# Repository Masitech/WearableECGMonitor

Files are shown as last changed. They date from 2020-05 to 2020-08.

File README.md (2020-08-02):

# WearableECGMonitor

ECG Monitor

result

result2

Project Report (110 pages) : https://www.mahmed.tech/wp-content/uploads/2020/05/Project_Report_MAhmed-converted-compressed.pdf 

## 1.1 Background

The IoT (internet of things) field in wearable healthcare has received a lot of attention in the last
few years due to advancement in computing paradigms: cloud computing, fog computing and
edge computing. Machine learning on the cloud has revolutionized traditional healthcare.
ECG monitors is not a new concept, it has been around the medical environment for many
decades. In the last few years, technology has started appearing in many wearable devices such
as smartwatches (apple watch 4+) and dedicated standalone products such as AliveCor's
KardiaMobile[3]. Most of the designs use 3 wires: 2 wires for bipotential input and the third wire
for body bias (common-mode rejection).

## 1.2 Aim

This project aims to design a low power battery operated wearable device with wireless
capability that can measure ECG from the bipotential single channel. The system should be
lightweight and small since it will be worn for a long period without a battery recharge.
Use professional tools & software platforms to design the system which is relevant in the
embedded systems industry.
Understand low level embedded systems and overcome problems which are specific to the
project using OEM datasheet/documentation. 

## 1.3 Objective

* Small custom-designed embedded arm cortex board using small SMD parts (0603 or
smaller).

* Develop low power wearable hardware that can be powered from a small battery.

* Develop onboard battery management system for charging lipo battery.

* Implement low power wireless capability using BLE.

* Design and implement embedded firmware using RTOS

* Use of UART, SPI, PWM, SAADC, Timers and interrupts in the firmware using
low-level hardware coding and API.

* Use of commercial development software and tools.

## 1.4 Technical Requirement / Tools

During the development phase of this project, the following tools were used, and it would be
essential to have access to these tools for future continuation of the work.

Software IDE: Keil uVision 5 

JLink Debugger / STLink Programmer: Used to flash the microcontroller.

J-Flash Light v6.54 (Tool to flash hex file)

nRF Bluetooth Connect App for Bluetooth Debugging (Android)

FTDI (USB to Serial) Module - UART communication

Eagle Autodesk to modify the schematic

Embedded C++/C, JavaScript, Bluetooth GATT, Max30003 AFE, Mbed OS, nrfSDK15

Optional: Tools that can be helpful.

SamacSys PCB Library: Excellent tool to get component footprint and save time

Notepad++ : Generic text editor, highly recommended

UART serial monitor: Arduino Serial Monitor, Termite

Plotting ECG Waveform: Arduino Plotter, Windisp (Custom Tool)

Multimeter, Oscilloscope & SMD soldering skills 

## 2. System Design 

Systemm Design

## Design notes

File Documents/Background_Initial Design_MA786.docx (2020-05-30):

Wearable ECG Monitor

University of kent

Masum Ahmed Ma786

2019

# 1.0.0 Introduction

The IoT (internet of things) field in wearable healthcare has received a lot of attention in the last few years due to advancement in computing paradigms; cloud computing, fog computing and edge computing. Machine learning on the cloud has revolutionized traditional healthcare which has led to the surge of new smart health devices. There is a non-invasive glucose monitor which can track glucose levels throughout the day. Omron is developing a smartwatch which can take blood pressure measurement using traditional methodology but at a much smaller scale. Google is using deep learning for detection of eye disease in diabetic patients with outstanding results [1].

Due to increasing world population especially the ageing population, there has been a massive strain on the healthcare system worldwide affecting millions of people. Traditional doctor-patient interaction has lost its effectiveness. The healthcare system as we know is changing from reactive treatment of illness at the hospital to preventive and personalized intervention. Artificial intelligence is getting increasingly sophisticated at emulating humans do so but more efficiently, quicker and cheaper. The potential for AI in the healthcare ecosystem is vast. Smart healthcare devices collect large amounts of processable data which can be examined in real-time and stored on a database to be viewed later. Interactions between doctor and patient are more efficient and patient-orientated since doctors can make better decisions.

The project aims to develop a small battery-powered ECG device that can be worn on the body.

While smart wearable ECG device is not as accurate as a full-scale 12 lead electrocardiograph, it has other significant advantages: it can be worn all day every day. It can collect data throughout the day across a wide range of activities. The more data it collects better preventive model can be established that is personalized to the patient. A large amount of data can also be used to establish patterns using machine learning and predict potential health problems before they arise.

## 1.1.0 Aim and Objectives

- Design a low power wireless ECG acquisition which can operate continuously for a day without recharging.
- Design an Algorithm to evaluate ECG and extract breathing rate, heart rate and heart rate variability.
- Use standard communication protocols such as BLT5 / Thread to connect to a gateway device (smartphone, raspberry pi etc.)
- Design an android based app to display the data in real-time.
- Setup cloud service for medical professionals to access the data remotely.

Deliverables:

- A low power microcontroller system with a biopotential sensor for ECG measurement. (Hardware)
- Custom buck-boost power circuitry with high efficiency and low idle current consumption.
- Voltage reference circuit to provide clean power reference for analogue measurements.
- Embedded firmware that can detect heart rate from ECG data & wireless communication using the Bluetooth 5.1 protocol on-chip.
- Implement features such as deep sleep, variable transmission power to save battery.
- An android app using java environment to display data in real-time.
- Web app using JavaScript to display historical data for health profession analysis.

# 2.0.0 Background Research

## 2.1.0 Theoretical Foundation: ECG Waveform

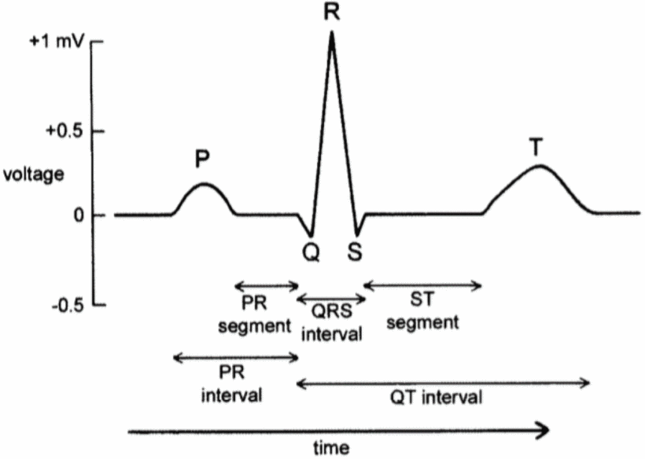
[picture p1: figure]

Figure 1 ECG waveform for one cardiac cycle

ECG measures the bio-potential generated by different contraction of the ventricles. The electrical impulse is generated in the sinoatrial node located in the atria [9]. The p wave as shown in figure 1 indicates atrial depolarization (atrial systole). There is a slight delay from the end of the P wave and the start of the QRS complex. This is caused by a cluster of cells called the atrioventricular node. This delay allows the atria to contract before the ventricle contracts. The QRS complex indicates ventricular contraction and depolarization (ventricular systole), this is caused by the electrical impulse moving from the AV node (atrioventricular node) through the bundle of His where it splits into the right-left bundle and then to the Purkinje fibres as shown in figure 2.

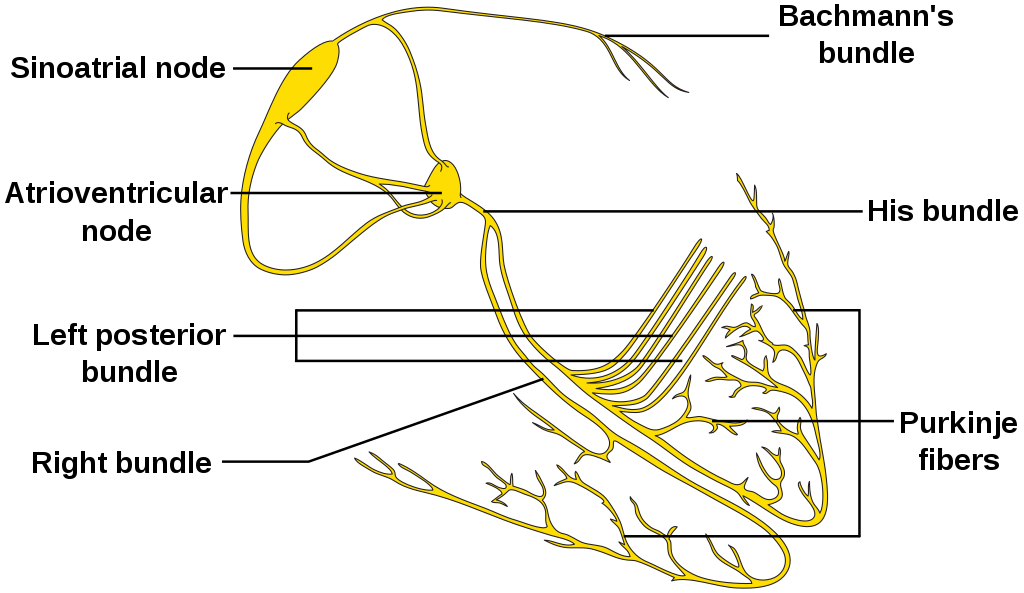
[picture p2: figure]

Figure 2 Electrical path of the heart during the cardiac cycle

In this project, I am only interested in the QRS complex, specifically the peak R amplitude from which the heart rate and heart rate variability will be calculated.

## 2.2.0 Technological State

Wireless technology and smart biosensors AFE (analogue front end) are the backbones of the smart healthcare system. There is a wide range of different wireless technology today supported by consumer devices: Wi-Fi, Bluetooth / BL Mesh, Thread, ANT, RFID, Zigbee, GSM/3G/4G. There are pros and cons to using all of these and specific technology is suited to certain project and environment.

There are two commonly used techniques in the industry to measure the heart rate, PPG (Photoplethysmography) and EEC (electrocardiography). PPG uses low-intensity infrared light to sense the change in blood flow during the cardiac cycle. The voltage signal from the receiver is inversely proportional to the volume of blood flowing. PPG is less accurate, more susceptible to motion artefact and consumes more power. The waveform of the PPG sensor contains fewer data related to the cardiac cycle [11][12].

## 2.3.0 Hardware Design and Implementation

There are multiple different approaches to designing analogue and digital hardware for ECG acquisition. One of the most advanced methods has been presented by Dr Shihui Yin et al from the University of Arizona who designed and fabricated the analogue hardware on 65nm CMOS logic [13]. It is extremely low power only 1.06µW during operation. Unfortunately, this is outside the scope of this project due to budget, time, tools limitation. It will be much easier to work with consumer IC’s and design custom PCB to integrate all the AFE’s and processing hardware. This approach was taken by theses research projects [8][14][15].

### 2.3.1 Microcontroller

ATmega328P (Arduino) 8bit microcontroller was used to acquire the ECG voltage data in [14][8] and MSP430 in [15]. The microcontrollers were chosen by the researchers because it has a lot of third-party libraries and interfacing them with a third-party device is well documented. However, the microcontrollers are slow only 16MHz, uses old 8 & 16-bit architecture, consumes a lot of power, the ADC resolution is limited to 8bits (atmega328P) and 10 bits on the MSP430 and most importantly Bluetooth is not integrated.

### 2.3.2 ECG Electrodes

Ag/AgC1 electrodes are widely used in ECG measurement due to their low skin to electrode contact impedance however, they are not suitable for continuous long-term measurement as it can irritate the skin and cause skin allergies [17]. An alternative dry electrode made from metal, conductive rubber or conductive fabric was found to be suitable for long term use [18][19].

### 2.3.3 Source of Noise

List of significant sources of noise in ECG data [22]

- Mains power lines produce 50Hz periodic interference.
- Movement can cause loss of contact between the skin and the electrode; this can result in a fast change in the potential difference in the signal which will result in false-positive readings.
- Muscle movement can cause noise from the electrical activity of the muscle.
- Respiration and general movement can cause baseline wander.

Signal to noise ratio can be improved by eliminating the above sources of noise. This can be done by implementing high and low pass filter and some software filtering.[8]

### 2.3.4 Acquiring ECG Data

“ECG input signal on the skin is very low in amplitude (<1 mV) and noisy. ECG voltage signal must be amplified, then high pass filtered to get rid of DC skin potential and battery effects. Then it must be low pass filtered to cut off high-frequency noise and mains interference” [16]. There seem to be many ways to achieve this. Traditionally electrodes would be connected to a series of operational amplifiers configured to perform the above function (amplify, high pass, low pass). However, this method is bulky because it requires a lot of components and consumes a significant amount of power.

The custom-designed integrated circuits prosed, in the study [14]. The researcher used the AD8232 IC which is a single chip with integrated OpAmps. The resistors connect to the pins of the AD8232 pins which can be altered to configure and set limits for the filters. Using the above configuration reduces PCB space however the design is still limited by the resolution of the ADC on the microcontroller.

### 2.3.5 EMI – Human Antenna Effect

The user body can act as an antenna which can pick up electromagnetic signals mostly in the range of 50 – 60 Hz common mode noise from mains electrical AC power lines. A large amount of electromagnetic interference is coupled to the user’s body through the skin [20]. The source of noise must be eliminated in hardware. The solution provided by the researcher uses the right leg as common noise input which can be rejected from the original differential ECG signal, more on this on selection 2.2.6 and why it is not viable according to [21].

### 2.3.6 Common Mode Rejection Ratio (CMRR)

Having a ground electrode to reduce noise is not suitable in a wearable device because it will introduce high leakage current during operation [21]. A system with high CMRR can be achieved by implementing an extra stage in the hardware signal processing. As mentioned in 2.2.5 the body is good at picking up common mode signals; noise that affects both electrodes equally. Achieving a system with a high common-mode ratio is important [22].

### 2.3.7 Data Storage

Continuous measurement of ECG will result in a lot of data. To avoid loss of data when the device is not connected to a suitable Bluetooth device or if the signal connection is lost data must be stored in a suitable place.

MicroSD card integration is simple and used by many research projects [8][15]. If the raw ECG data is not kept rather the induced HR, then it will be suitable to use the onboard flash in the microcontroller itself. Micro SD card may not be suitable in a low power wearable device. It can consume around 100mA at 3.3V. An alternative option would be to use NOR flash chips.

### 2.3.8 Sampling Frequency

It was determined sampling frequency low as 50Hz can be used to obtain HRV by software interpolation [23]. The researcher tested a range of sampling frequency from 5KHz to 50Hz and run statistical tests on each of the acquired data. The researcher also noted the R peaks were slightly distorted due to low sampling frequency. The optimal range of sampling rate for spectral analysis of HRV parameters is between 250 and 500 Hz [24].

## 2.4.0 Market Research

### 2.4.1 Commercial Products

Amazfit Health Band 1S Is a PPA based smart band with an ECG sensor. It uses PPA technology to continuously monitor the heart rate if it detects arrhythmia then it alerts the user and asks them to take an ECG reading by placing a finger on top of the band. The data is sent to the cloud which is then processed by AI. The data can be accessed by the user (free for the first 6 months). The device is manufactured and developed by a Chinese company and is not widely adopted in the west.

Welch Allyn TAGecg sensor Is an ECG based chest sensor which continuously records the ECG of the user. It examines the heart rate and has built an algorithm in the local system to detect arrhythmia. The data is also synced to the cloud where it can be further examined by the medical profession. The device is manufactured and developed by Welch Allyn an American company who develops a medical device for private healthcare in America.

# 3.0.0 System Design

The system will have bipotential ECG AFE sensor which will take differential measurement from 3 wire electrode (ECG P, ECG N). It will be powered from the +3.3V and +1.8V rail. The ECG sensor will be interfaced to the microcontroller via SPI (Serial Peripheral Interface).

To reduce PCB space and power consumption a microcontroller with wireless capability will be utilised. It will be interfaced with NOR flash to store data while the system is not connected to an external Bluetooth master node. It will be time synced relative to the connected master node since it does not have a real-time clock. Alongside the ECG data, relative timing information will be stored. This information is important to calculate the heart rate & heart rate variability of the user.

The embedded hardware will connect to a smartphone via Bluetooth and send its stored data. This data will be temporarily stored on the phone then uploaded to a server connected to the internet. There will be a companion app on a smartphone which will display current data send by the embedded hardware and historic data stored on an online database. For third party public access there will be a web portal where historic data can be viewed.

The system will have the ability to show live ECG and temperature data in real-time through the android application. At this stage, the mobile phone will not be doing any preprocessing just acting as a monitor for the data.

The cloud system will be set up on a separate computer connected to the internet. It will use MySQL database to store the data which can be accessed on via time and key events. The system will only focus on the single-user system to reduce design complexity.

Website hosted on a server will be utilized to develop a web portal to access data from the database for public usage. The system will be protected from unauthorised access by user login.

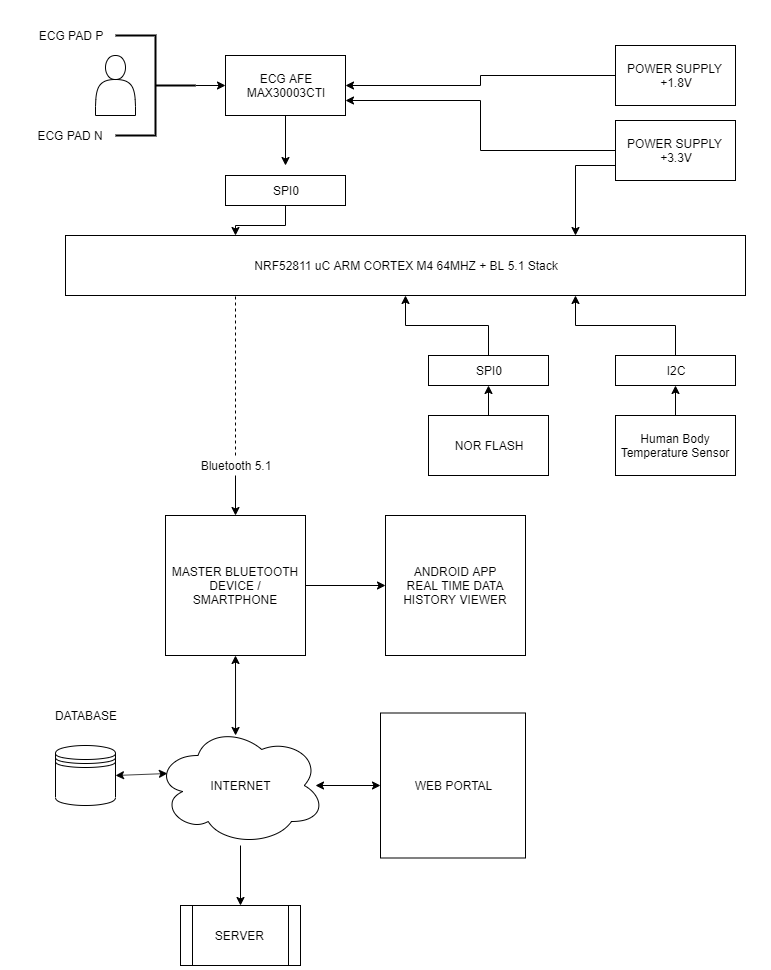
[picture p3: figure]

Figure 3 High-level system architecture diagram

## 3.1.0 Microcontroller

Espressif ESP32 WIFI & BLE is an alternative option since I have used this soc before, however, this would not fit the project since the power consumption during transmission is too high 100mA vs ~4.6mA (nRF52811). The footprint of the IC is too small to solder by hand and the processor is over specced for what I need it for. 240mhz @ dual-core is too much power. It also implements an older protocol: Bluetooth 4.2.

Nordic Semiconductor nRF52811 is a low power 64mhz arm cortex M4 based microcontroller with Bluetooth 5.1 protocol, including Long Range and Direction Finding, 802.15.4, Thread and Zigbee in a 6mm² 48pin QFN package. The microcontroller has low power consumption during idle and only 4.6mA during transmission at 0dB this makes it ideal for wearable devices.

When designing with this microcontroller the SPI1 instance cannot be used while using I2C peripheral because they both share the base memory address.

I have chosen this microcontroller over Arduino(atmega328P) and mbed (lpc1768) because it has the Bluetooth stack integrated into the microcontroller. The datasheet is comprehensive and there is a lot of online support. In industry, semiconductor devices are widely used where esp32 and Arduino are limited to maker and research projects due to licencing incompatibility.

## 3.2.0 Integrated Biopotential Sensor

BMD101 Is a popular IC used in commercial ECG band due to its size and performance, however, availability is non-existent in the EU/UK/US market. The datasheet is only 14 pages and covers the basic aspects of the IC.

MAX30003CTI+ Ultra-Low Power, Single-Channel Integrated Biopotential dual electrode. It’s a complete analogue front-end solution for wearable applications. It packs all the operational amplifiers internally in a small QFN package. This is an improvement upon Dr B. Babusiak analogue design [8] because it saves PCB space, power-efficient and has higher CMRR.

The IC has built-in R-R detection which uses the Pan-Tompkins algorithm [2] to determine the heart rate. However raw data can be sent to the microcontroller by changing the registers. It simplifies filtering by internally incorporating a low and high pass filter reducing the external components. The device can also be configured to output raw 15.5bit ADC reading (sample and hold) without any modification.

Baseline wander is an issue with ECG (low-frequency noise) which can be expensive (compute time) in software to fix. The AFE tries to take care of this at a hardware level. The gathered data has a high signal to noise ratio (SNR). There are three recommended options for the cut off frequency: 4.4Hz, 0.4Hz, and 0.04Hz. Setting the cut off frequency to 4.4Hz provides the most motion artefact rejection, the trade-off is waveform quality.

The device’s ECG channel contains an input amplifier that provides low-noise, fixed-gain amplification of the differential signal (ECG Positive, ECG Negative), rejects differential DC voltage due to electrode polarization, rejects common-mode interference primarily due to AC mains interference, and provides high input impedance to guarantee high CMRR (Common Mode Rejection Ratio).

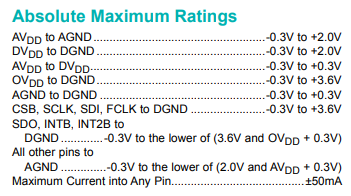
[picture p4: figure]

Figure 4 Pin input voltage rating from max30003 datasheet

The datasheet (figure 4) shows AVDD -> AGND must be <+2.0V and DVDD -> DGND <+2.0V this means I need dual voltage rails 3.3V and 1.8V since the AFE is not high power I will use low IQ (quiescent current) low dropout linear regulator (LDO). There are 2 different grounds, AGND & DGND. The ground will be connected to each other by a 0 ohms resistor.

##### 3.2.1 Lead Bias

The ECG AFE limits the input of ECGP and ECGN DC input common-mode range to VMID ±150mV. This means if there’s a significant bias voltage it can result in the signal getting clipped at VMAX and VMIN resulting in data loss. This can be fixed using external lead biasing resistor, fortunately, this IC has internal selectable lead biasing resistor: 50MΩ, 100MΩ and 200MΩ CNFG_GEN (0x10) register can be used to select a configuration.

##### 3.2.2 Interfacing ECG AFE with an MCU

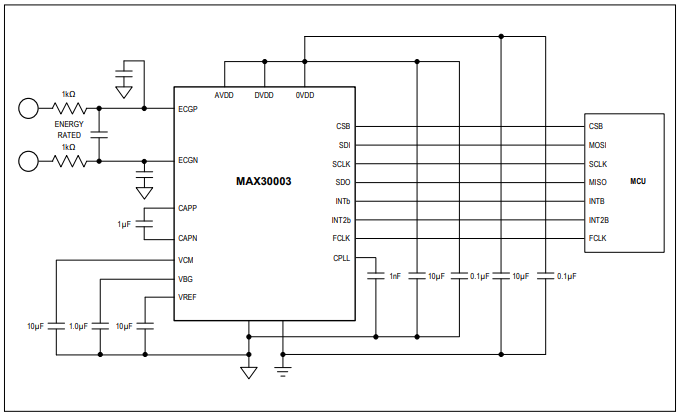
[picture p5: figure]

Figure 5 ECG AFE interfacing with a generic micro-controller

Integration to nrf52811 microcontroller GPIO pin can be configured as required in software, therefore, it does not matter which pin the corresponding pins connect to. MOSI, SCLK, MISO are SPI specific pins while INTb and INTa are interrupted pins to indicate when data is ready. FCLK is the clock to max30003 this will be a GPIO pin controlled under interrupt to change the clock edge. CSB is chip select to reliable / disable SPI communication there can be multiple devices on the SPI interface.

Name | Function
CBS | Active low chip select input. enables the serial interface
SDI | Serial Data Input. SDI is sampled into the device on the rising edge of SCLK when CSB is low
SCLK | Serial Clock Input. Clocks data in and out of the serial interface when CSB is low
SDO | Serial Data Output. SDO will change state on the falling edge of SCLK when CSB is low. SDO is high z when CSB is high.
INTb | Interrupt Output. INTB is an active low-status output. It can be used to interrupt an external device.
INT2b | Interrupt 2 Output. INT2B is an active-low status output. It can be used to interrupt an external device.
FCLK | External 32.768kHz Clock that Controls the Sampling of the Internal Sigma-Delta Converters and Decimator.

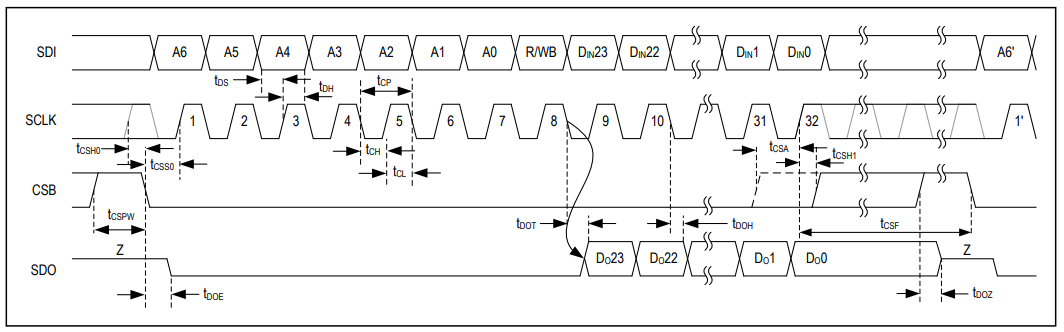
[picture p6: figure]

The timing characteristics (figure 6) is used to write the SPI driver software. It outlines timing limits and pins logic during operation, it also outlines when the data is ready to be read and when to write. The full table can be accessed on page 7 of the datasheet.

Figure 6 Timing characteristics max30003 datasheet p7

## 3.3.0 Power Supply

For the project, it makes sense to use a rechargeable battery. Lithium-ion polymer battery (LIPO) comes in small packages with a large capacity. Making it suitable for wearable / portable device since it can store a lot of power in a small size. The short circuit current for LIPO battery is a lot higher than alkaline batteries, therefore, can cause fires easily if not monitored strictly [7]. The proposed design to monitor the battery voltage while charging. This is a backup protocol in case the charging IC is misbehaving see figure 7 for power supply design diagram.

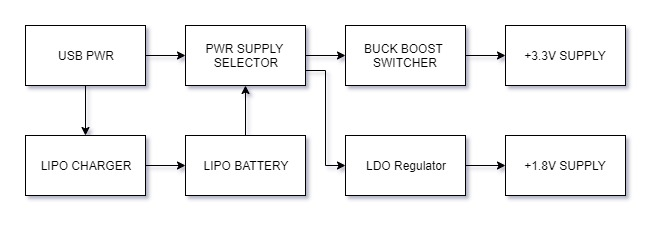
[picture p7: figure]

Figure 7 Power supply system design

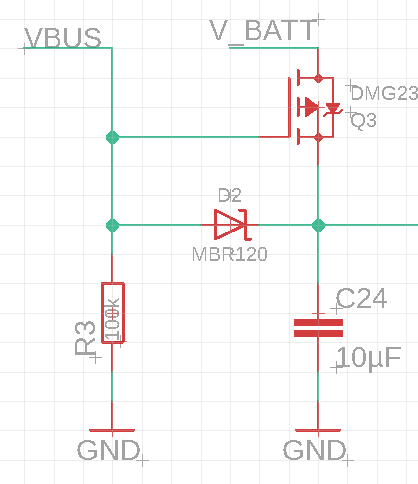
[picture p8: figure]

The normal battery level is 3.7V and it can range from 4.2V to 2.2V. Since the system voltage level ist at 3.3V, the power supply must be in buck configuration above 3.3V and in boost configuration below 3.3V. When the USB charging cable is connected, the system will be powered from USB power rather than battery power. This resolves the issues of charging the battery while providing power. This is implemented using N channel MOSFET (Q3) and a diode. When the USB cable is connected Q3 is disabled since gate voltage is at VBUS, this cuts off the V_BATT power in. When the USB cable is disconnected the gate voltage is GND (pulled down by R3 resistor) which enables Q3. D2 diode stops the current flowing in the opposite direction note figure 8 for further details.

Figure 8 Digital logic to select USB power over LIPO power if it is present.

### 3.3.1 Battery Charger

To charge the LIPO battery MCP73831 IC will be used from microchip because it requires minimal external components and it is in a footprint that can be soldered by hand without too much effort. This is different from the one used in [8], MCP7337 was not chosen because it consumes a lot more PCB space. mcp73837 has a feature that is not available on the mcp73837 due to limited pins. To get the same level of capability as the bigger brother I will not be following the recommended application implementation design since I want to control the charger IC using the microcontroller. Unfortunately, this IC does not have an enable disable pin to control the IC unlike mcp73837 and the status pin is configured to connect to an LED. I want the microcontroller to know when the battery is charged and when it is charging. Figure 9A shows a typical application design and figure 9B shows the modified design.

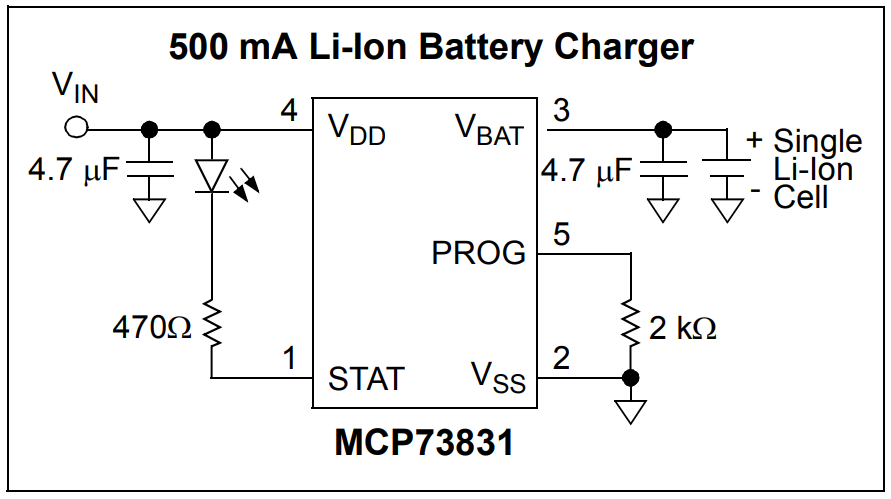
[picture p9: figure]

Figure 9A Typical design implementation of MCP73831

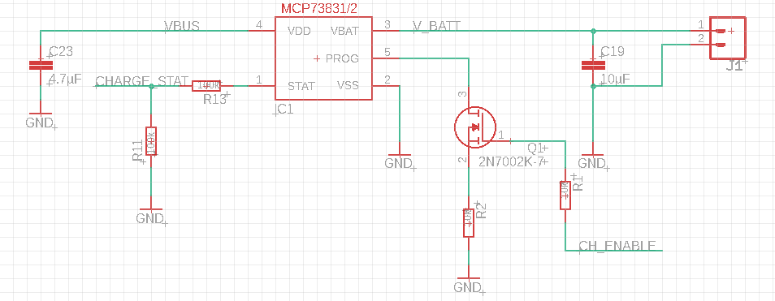
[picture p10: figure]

Figure 9B Custom design implementation proposal

I have used a P channel MOSFET with the gate connected to a GPIO pin on the microcontroller. The source to base resistance is around 1 ohm so it should have minimal effect on the charging current which determined by the formula (1) (1 ) Ireg= (1000v)/(Rprog) A charge current programming resistor must be connected from PROG to VSS. If the PROG pin is open or floating, the MCP73831/2 is disabled and the battery reverse discharge current is less than 2 µA extract from mcp73831 datasheet. I am not using reverse battery protection diode because it will consume power while idle and the voltage drop is significant.

Where Ireg = in milliohms, Rprog = in kilo-ohms.

Charge status pin is tri-state and requires a pull-down or a pull-up. During the logic high, the status pin VDD is same as STAT which can be as high as 5V, therefore, I have used a resistor divider.

## 3.4.0 Software Architecture

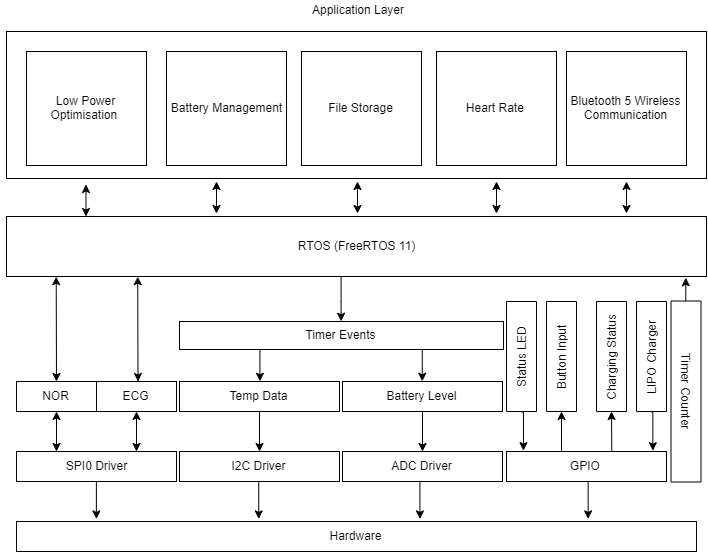
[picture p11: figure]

Figure 10: Software design layers

The embedded software will consist of subprograms which will be responsible for different tasks. Figure 10 outlines the smaller components of the software breaking it down into layers bottom being closer to the hardware. The higher layers are general-purpose code, they are generally less restricted by the hardware making it more portable.

FreeRTOS will be used as the real-time operating system because it is free and open-source. On top of the RTOS will be my custom application code among the Bluetooth stack from a Nordic semi (manufacture). Below the RTOS will be the hardware determined code, responsible for controlling the peripherals on the microcontroller.

## 3.5.0 Android App

Andriod studio IDE and java programming language will be used to create the android application. The resources such as images and gfx design will be obtained from openGFX package. It will be my first time developing an android application; therefore, extra time was given on the grant chart to learn java and JavaScript. Java was chosen over Kotlin because it has more resources and my course teaches java. JavaScript will be used to design buttons, logos, animation etc. I hope to interface the app with Bluetooth hardware on the android phone and connect to the embedded hardware.

## 3.6.0 Bluetooth 5 Communication

Bluetooth is a standardised protocol for transmitting and receiving data wirelessly on the 2.4GHz channel. Its secure, short-range, low power and cost and requires minimal external hardware. Bluetooth has standardised test of rules and specification which differentiates it from other standards: WIFI, ZigBee, ANT and Thread.

The BL is standard is published and maintained by the bluetooth.com organisation. The specification outlines all aspects of Bluetooth however its 2985 pages long.

Bluetooth network utilises master/slave model to control when the device can transmit data. Every Bluetooth device has a unique 48-bit MAC address (BD_ADDR) presented in 12-digit hexadecimal format. Most significant half of the address identifies the manufacturer and the lower 24bit is the uniqueness. MAC address is used in software to identify hardware and keep track of communication between that hardware and itself. The microcontroller I will be using has Bluetooth integrated. I will be using the Bluetooth stack provided by the manufacturer (Nordic Semiconductor).

# 4.0.0 Development Tools

## 4.1.0 Keil 5 MDK

Keil will be used as programming and flashing platform because it provides good compatibility with the chosen microcontroller and I have used this IDE during my year in industry. I will be using the NRF SDK on this platform. Among their own software library integrated into the IDE itself. Keil allows programming using debuggers such as Segger JLINK however the cost of a debugger is several times the budget of this project.

## 4.2.0 Windisp UART Communication

Windisp is a serial communication terminal, I will be using this tool extensively during development. It will communicate with the embedded system using UART and display data in a readable format. Unfortunately, it’s not able to do graphs directly but it is able to create.CVS files; using excel I will be able to create trend files and graphs.

## 4.3.0 Programming Custom Board

The microcontroller cannot be programmed via UART (RS232). Which is a major limitation because it means I must use SWDIO pin to program the device. This requires external tools which are very expensive. The NRF52DK has a secondary processor used just for programming and interfacing it to MBED. I will be utilising the dev kits secondary processor to flash my microcontroller.

# 5.0.0 Risk Analysis

Risk | Precaution Taken to Minimise Risk
Out of stock parts | All the parts used in the project can be sourced from multiple different companies as well as the manufacturer.
Incompatible software | I have downloaded and installed all the software already to make sure its compatible with my system
Delay in a custom board | I will be using development boards while the custom board manufactured and assembled.
Damaged PCB | I have given myself time to manufacture 2 versions of the PCB.
Design / Logic Fault | Before starting the layout, the schematic will be checked to make sure everything is connected correctly.
Running out of time | I am planning to implement an incremental development process. Core things like hardware and ECG data will be a priority then will come the extra features.
Hard stuck coding | I will use a tool called windisp to debug the code to find where the problem is. Also, debuggers tools such as Segger JLink integrated on the dev board can be used to resolve coding issues.
Damaging boards while soldering | I will order multiple copies of the same version of the PCB if one gets damaged it will not affect the progression of the project.

# 6.0.0 Project Plan and Budget

## 6.1.0 Bill of Material

Quantity | Parts ID | Price (1 unit) | Supplier | Stock Code
2 | NRF52811 | £3.19 | Mouser | 949-NRF52811-CAAA-R
2 | MAX30003 | £7.33 | Mouser | 700-MAX30003CTI+
1 | AT25QF128A-SHB-T | £1.25 | Mouser | 988-AT25QF128A-SHB-T
1 | MAX30205 | £1.92 | Mouser | 700-MAX30205MTA+
| SMD Resistors | £8.00
| SMD Cap | £8.00
| SMD Inductor | £5.00
2 | MCP73831 | £0.47 | Mouser | 579-MCP73831T-2ACIOT
1 | Turnigy 200mAh | £1.89 | Hobby King | 9067000498-0
2 | LDO | £0.25 | Mouser | 579-MCP1811AT-042/TT
1 | Max30003 DK | £19 | Mouser | 700-MAX30003WING
5 | PCB | £4
1 | JLINK Programmer | - | -
1 | Nrf5240 UBB Dev Board | £8.52 | Mouser | 949-NRF52840-DONGLE
| Total | £94.81 | -

## 6.2.0 Gantt Chart

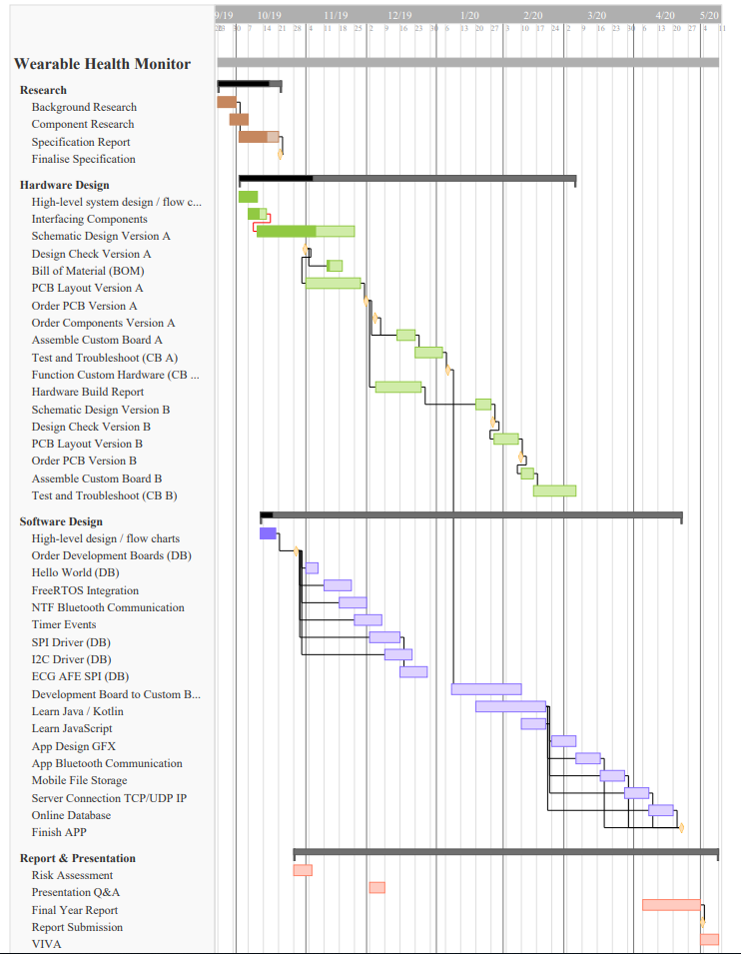
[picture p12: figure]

# 7.0.0 References

[1]

Gulshan V, Peng L, Coram M, et al. Development and Validation of a Deep Learning Algorithm for Detection of Diabetic Retinopathy in Retinal Fundus Photographs. JAMA. 2016;316(22):2402–2410. doi:10.1001/jama.2016.17216

[2]

Pan, J. and Tompkins, W. (1985). A Real-Time QRS Detection Algorithm. IEEE Transactions on Biomedical Engineering, BME-32(3), pp.230-236.

[3]

P., Chiang, P., Tarng, D. and Yang, C. (2018). Mathematical derivation, circuits design and clinical experiments of measuring blood flow volume (BFV) at arteriovenous fistula (AVF) of hemodialysis (HD) patients using a newly developed photoplethysmography (PPG) sensor. 2018 19th International Symposium on Quality Electronic Design (ISQED).

[4]

Arun, U., Natarajan, S. and Rajanna, R. (2018). A Novel IoT Cloud-based Real-Time Cardiac Monitoring Approach using NI myRIO-1900 for Telemedicine Applications. 2018 3rd International Conference on Circuits, Control, Communication and Computing (I4C).

[5]

Rahman, A., Rahman, T., Ghani, N., Hossain, S. and Uddin, J. (2019). IoT Based Patient Monitoring System Using ECG Sensor. 2019 International Conference on Robotics, Electrical and Signal Processing Techniques (ICREST).

[6]

Nurdin, M., Hadiyoso, S. and Rizal, A. (2016). A low-cost Internet of Things (IoT) system for multi-patient ECG's monitoring. 2016 International Conference on Control, Electronics, Renewable Energy and Communications (ICCEREC).

[7]

Vitols, K. (2015). Lithium ion battery parameter evaluation for battery management system. 2015 56th International Scientific Conference on Power and Electrical Engineering of Riga Technical University (RTUCON).

[8]

Babusiak, B., Gala, M. and Borik, S. (2014). Hardware design of ECG data logger. 2014 ELEKTRO.

[9]

Anthony Dupre MS, MS Sarah Vincent, Paul A. Iaizzo, "Basic ECG Theory Recordings and Interpretation", Chapter Handbook of Cardiac Anatomy Physiology and Devices,

[10]

Chavdar Levkov, Georgy Mihov et al, "Removal of power-line interference from the ECG: a review of the subtraction procedure", Biomedical Engineering Online, 2005.

[11]

Lu, G., Yang, F., Taylor, J. and Stein, J. (2009). A comparison of photoplethysmography and ECG recording to analyse heart rate variability in healthy subjects. Journal of Medical Engineering & Technology, 33(8), pp.634-641.

[12]

Lu, G. and Yang, F. (2009). Limitations of Oximetry to Measure Heart Rate Variability Measures. Cardiovascular Engineering, 9(3), pp.119-125.

[13]

Yin, S., Kim, M., Kadetotad, D., Liu, Y., Bae, C., Kim, S., Cao, Y. and Seo, J. (2017). A 1.06 μw smart ecg processor in 65 nm cmos for real-time biometric authentication and personal cardiac monitoring. 2017 Symposium on VLSI Circuits.

[14]

Tanweer, M. and Halonen, K. (2019). Development of wearable hardware platform to measure the ECG and EMG with IMU to detect motion artifacts. 2019 IEEE 22nd International Symposium on Design and Diagnostics of Electronic Circuits & Systems (DDECS).

[15]

Chen, W., Chen, Y., Chou, C. and Fang, W. (2015). An EEG analog front-end design with wireless communication module for a portable EEG monitoring system. 2015 IEEE 5th International Conference on Consumer Electronics - Berlin (ICCE-Berlin).

[16]

Lacirignola, F. and Pasero, E. (2017). Hardware design of a wearable ECG-sensor: Strategies implementation for improving CMRR and reducing noise. 2017 European Conference on Circuit Theory and Design (ECCTD).

[17]

Ju-Yeoul Baeka, Jin-Hee An, Jong-Min Choi, Kwang-Suk Park, Sang-Hoon Lee. "Flexible polymeric dry electrodes for the long-term monitoring of ECG," Sensors and Actuators A: Physical, vol. 143, 2008, pp. 423-429.

[18]

S. H. N. Chang, Y. Ryu, K. Seunghwan, "Conductive rubber electrode for wearable health monitoring," in Proceesing of the 2005 IEEE Engineering in Medicine and Biology 27th Annual Conference, Shanghai, China, 2005. pp. 3479-3481.

[19]

Carey R. Merritt, H. Troy Nagle, and Edward Grant, "Fabric-based active electrode design and fabrication for health monitoring clothing," IEEE Transactions on information technology in biomedicine. vol. 13, 2009, pp.274-280.

[20]

Acharya, V., 2011. Improving common-mode rejection using the right-leg drive amplifier. Texas Instruments, pp.1-11.

[21]

Lacirignola, F. and Pasero, E. (2017). Hardware design of a wearable ECG-sensor: Strategies implementation for improving CMRR and reducing noise. 2017 European Conference on Circuit Theory and Design (ECCTD).

[22]

A. S. Barhatte, R. Ghongade, and S. V. Tekale, “Noise analysis of ECG signal using fast ICA,” 2016 Conference on Advances in Signal Processing (CASP), 2016.

[23]

S. Mahdiani, V. Jeyhani, M. Peltokangas, and A. Vehkaoja, “Is 50 Hz high enough ECG sampling frequency for accurate HRV analysis?” 2015 37th Annual International Conference of the IEEE Engineering in Medicine and Biology Society (EMBC), 2015.

[24]

G. D. Pinna, R Maestri, A. Di, R. Colombo, G. Minuco, "The accuracy of power spectrum analysis of heart rate variability from annotated RR lists generated by Holter systems", Physiological Measurement, vol. 15, no. 2, pp. 163-179, May 1994.

Section I: Project details
Project title: | Wearable ECG Monitor
Planned start date: 23/09/2019 | | Planned end date: 28/04/2020
Funder: | University of Kent

Section II: Applicant details
Applicant name: | Masum Ahmed
Department: | EDA
Email: Masum Ahmed | | Telephone number: 07410124124
Contact address: | 17 channel close Folkestone ct196qn

Applicant signature | M.Ahmed | Date | 16/10/2019

Section III: Students only
Supervisor: S. Hoque
Undergraduate ☒ | Masters ☐ | | Doctorate ☐ | Other (please specify)

Supervisor name | | Date
Supervisor signature

School REAG rep signature | | Date

If any question in Section IV(A) are answered ‘yes’:

1. Contact Nicole Palmer (University Research Ethics & Governance Officer) for advice
2. Send a copy of ethical approval to the Faculties Support Office, once received

If any questions in Section IV(B) are answered ‘yes’:

1. Complete full application form
2. Send to the Faculties Support Office for review by the Research Ethics Advisory Group (REAG)

If all questions in Section IV(A) and IV(B) are answered as ‘no’, send the completed and signed form to the Faculties Support Office.

Declaration: Please note that it is your responsibility to follow, and to ensure that, all researchers involved with your project follow accepted ethical practice and appropriate professional ethical guidelines in the conduct of your study. You must take all reasonable steps to protect the dignity, rights, safety and well-being of participants. This includes providing participants with appropriate information sheets, ensuring informed consent and ensuring confidentiality in the storage and use of data.

Section IV: Research Checklist

Please answer all questions by ticking the appropriate box:

A) Research that may need to be reviewed by an NHS Research Ethics Committee, the Social Care Research Ethics Committee (SCREC) or other external ethics committee (if yes, please give brief details as an annex) | YES | NO
Will the study involve recruitment of patients through the NHS or the use of NHS patient data or samples? | ☐ | ☒
Will the study involve the collection of tissue samples (including blood, saliva, urine, etc.) from participants or the use of existing samples? | ☐ | ☒
Will the study involve participants, or their data, from adult social care, including home care, or residents from a residential or nursing care home? | ☐ | ☒
Will the study involve research participants identified because of their status as relatives or carers of past or present users of these services? | ☐ | ☒
Does the study involve participants aged 16 or over who are unable to give informed consent (e.g. people with learning disabilities or dementia)? | ☐ | ☒
Is the research a social care study funded by the Department of Health? | ☐ | ☒
Is the research a health-related study involving prisoners? | ☐ | ☒
Is the research a clinical investigation of a non-CE Marked medical device, or a medical device which has been modified or is being used outside its CE Mark intended purpose, conducted by or with the support of the manufacturer or another commercial company to provide data for CE marking purposes? (a CE mark signifies compliance with European safety standards) | ☐ | ☒
Is the research a clinical trial of an investigational medicinal product or a medical device? | ☐ | ☒

If the answer to any questions in Section IV(A) is ‘yes’, please contact the Research Ethics & Governance Officer for further advice and assistance.

B) Research that may need full review by the Sciences REAG | YES | NO
Does the research involve other vulnerable groups: eg, children; those with cognitive impairment? | ☐ | ☒
Is the research to be conducted in such a way that the relationship between participant and researcher is unequal (eg, a subject may feel under pressure to participate in order to avoid damaging a relationship with the researcher)? | ☐ | ☒
Does the project involve the collection of material that could be considered of a sensitive, personal, biographical, medical, psychological, social or physiological nature. | ☐ | ☒
Will the study require the cooperation of a gatekeeper for initial access to the groups or individuals to be recruited (eg, headmaster at a School; group leader of a self-help group)? | ☐ | ☒
Will it be necessary for participants to take part in the study without their knowledge and consent at the time? (eg, covert observation of people in non-public places?) | ☐ | ☒
Will the study involve discussion of sensitive topics (eg, sexual activity; drug use; criminal activity)? | ☐ | ☒
Are drugs, placebos or other substances (eg, food substances, vitamins) to be administered to the study participants or will the study involve invasive, intrusive or potentially harmful procedures of any kind? | ☐ | ☒
Is pain or more than mild discomfort likely to result from the study? | ☐ | ☒
Could the study induce psychological stress or anxiety or cause harm or negative consequences beyond the risks encountered in normal life? | ☐ | ☒
Will the study involve prolonged or repetitive testing? | ☐ | ☒
Will the research involve administrative or secure data that requires permission from the appropriate authorities before use? | ☐ | ☒
Is there a possibility that the safety of the researcher may be in question (eg, international research; locally employed research assistants)? | ☐ | ☒
Does the research involve participants carrying out any of the research activities themselves (i.e. acting as researchers as opposed to just being participants)? | ☐ | ☒
Will the research take place outside the UK? | ☐ | ☒
Will the outcome of the research allow respondents to be identified either directly or indirectly (eg, through aggregating separate data sources gathered from the internet)? | ☐ | ☒
Will research involve the sharing of data or confidential information beyond the initial consent given? | ☐ | ☒
Will financial inducements (other than reasonable expenses and compensation for time) be offered to participants? | ☐ | ☒
Are there any conflicts of interest with the proposed research/research findings? (eg, is the researcher working for the organisation under research or might the research or research findings cause a risk of harm to the participants(s) or the researcher(s) or the institution?) | ☐ | ☒

If the answer to any questions in Section IV(B) is ‘yes’, please complete the full application form and send to the Faculties Support Office

C) Security Sensitive Material | YES | NO
Does your research involve access to or use of material covered by the Terrorism Act? (The Terrorism Act (2006) outlaws the dissemination of records, statements and other documents that can be interpreted as promoting and endorsing terrorist acts. By answering ‘yes’ you are registering your legitimate use of this material with the Research Ethics Advisory Group. In the event of a police investigation, this registration will help you to demonstrate that your use of this material is legitimate and lawful). | ☐ | ☒

Wearable ECG Monitor Masum Ahmed

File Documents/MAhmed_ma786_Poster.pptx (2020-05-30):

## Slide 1

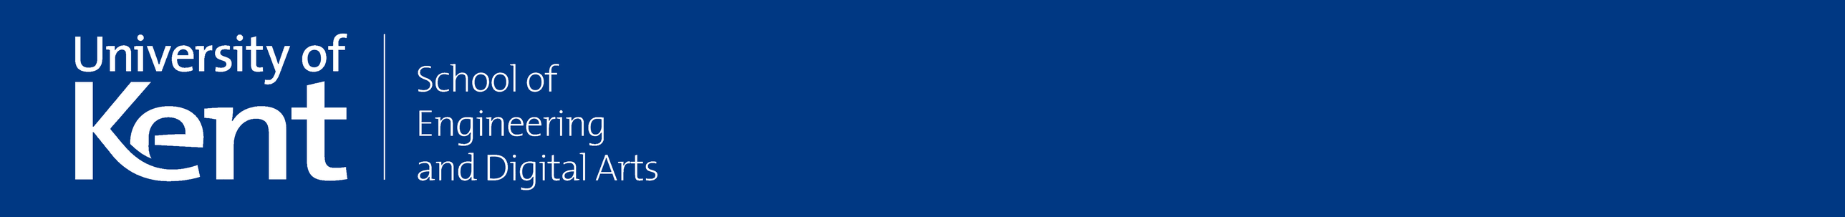
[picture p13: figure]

Wearable ECG Monitor

By M Ahmed Supervisor: Dr S Hoque

INTRODUCTION

The IoT (internet of things) field in wearable healthcare has received a lot of attention in the last few years due to advancement in computing paradigms: cloud computing, fog computing and edge computing.
This project aims to develop a highly integrated battery-powered wearable embedded system with wireless capability that can measures ECG from bipotential input. To get an understanding of engineering development that moves past the educational / preconfigured hardware module and into the industrial territory. Implementing custom design at chip-level using manufacture provided datasheets.

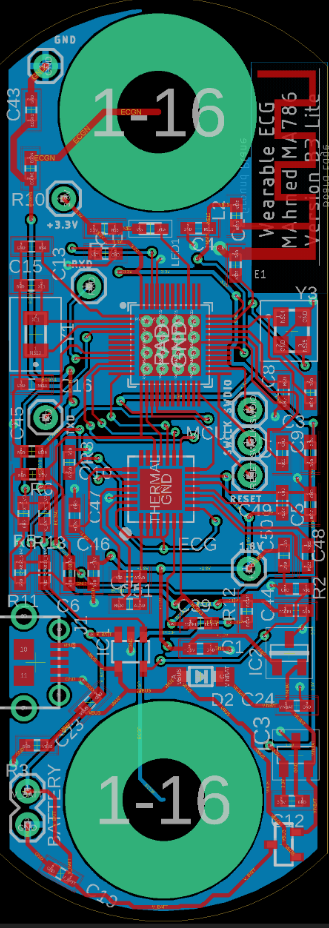
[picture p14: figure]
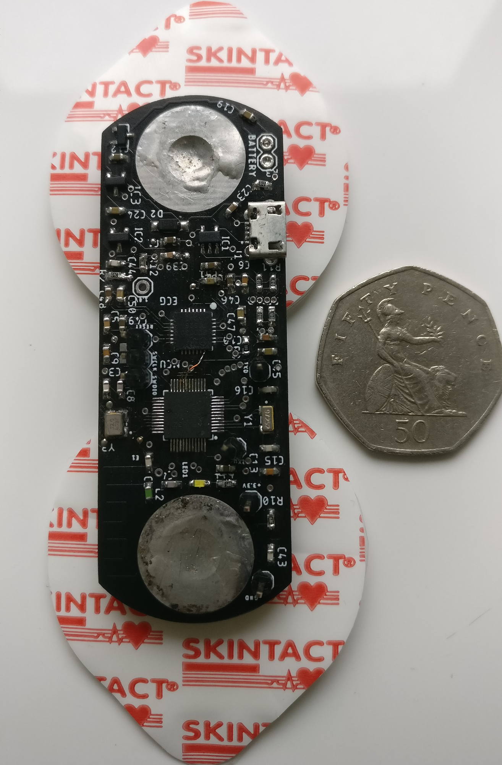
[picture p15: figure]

SYSTEM ARCHITECTURE

Top-level design of the system outlines the different subsystems and how they are interconnected.
At the heart of the system is the ECG analogue front end and the Nordic semiconductor Bluetooth microcontroller.
The system interfaces with a human using 2 wires, positive and negative leads to take differential measurements. The 15bit analogue to digital data is pre-processed using hardware low and high pass filters. The data is accessed from the FIFO buffer by the microcontroller once it reached 4 or more samples via SPI interface. The microcontroller implements MBED RTOS which manages various task pseudo- simultaneously. The microcontroller is responsible for: system power management, Bluetooth packet advertisement using GAP protocol, streaming signed normalised ECG voltages, heart rate and battery level information using GATT service.

qRS

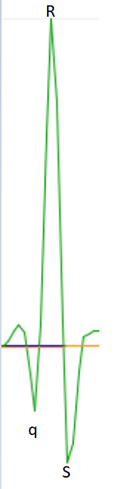
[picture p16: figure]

TEST RESULT

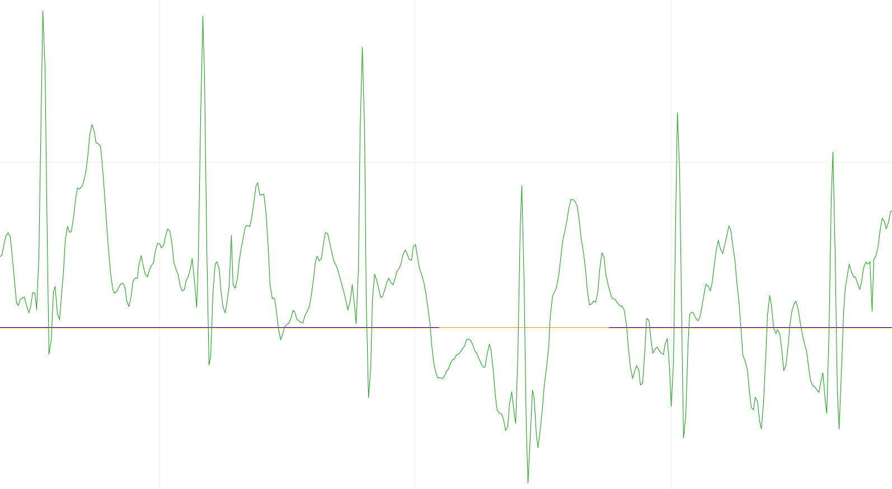
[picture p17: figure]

TEST | | Result
ECG Data Acquisition | | PASS
BLE (HR, Battery GATT) | | PASS
BLE ECG (Custom GATT) | | PASS
Peak Power Consumption | | 7.6mA
Idle Power Consumption | | <1mA
Power Efficiency | | 88%
Battery life** | | 263 Hours
Wearability (75*25*1.6mm) | | 13 Grams
Compatibility | | 2/3 **

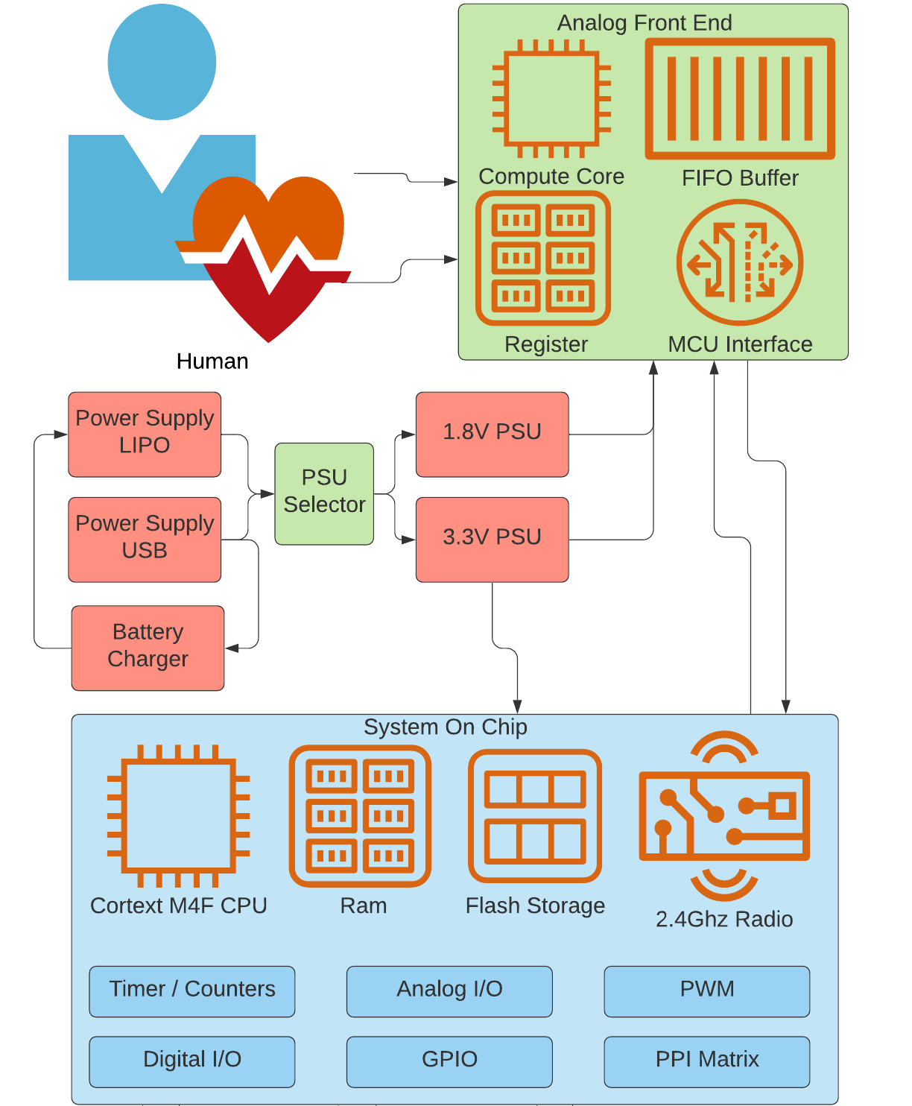
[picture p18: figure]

It is estimated by WHO 17 million people die of cardiovascular disease-related every year. To put that in perspective, it’s the equivalent of the population of the Netherlands. This project developed a wearable device that can measures a human hearts electrical activity using a current-gen chip technology from maxim semiconductor. The data can be transmitted to any supporting Bluetooth device for monitoring. It is anticipated in the future wearable health devices will be widely adopted among consumer users, as it will not just benefit the doctors and patient but help tackle pandemics.

Extensive hardware, software and data quality tests have been performed to ensure the system works under a range of different conditions and variables.
The system performed well with low power consumption during data streaming over Bluetooth low energy. The system uses GATT which allows developers to write software apps for the ECG monitor without direct access to the code. The system was custom designed in eagle software, manufactured in China and assembled in the engineering lab. The system designed meets the current aims, objective and deliverable with further changes to make the system more robust
**2000mAh Lithium-ion polymer battery was used for testing.

PRESS RELEASE

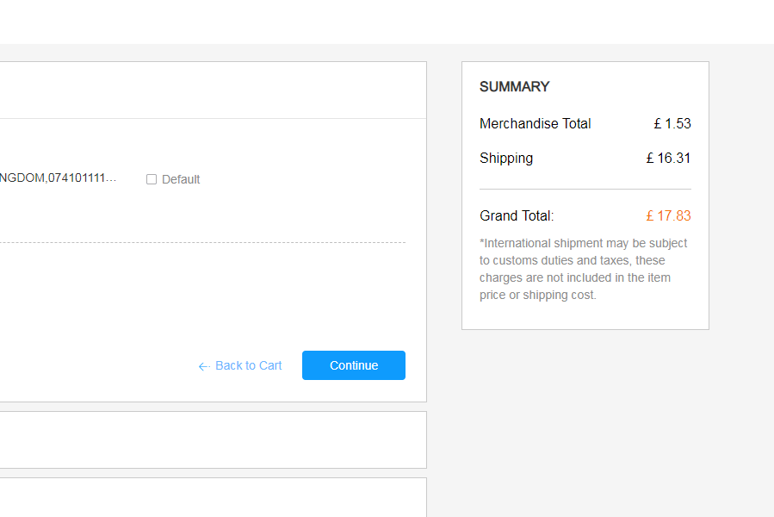
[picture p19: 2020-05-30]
Hardware/Version B1 Advance nrf52832/CAMOutputs/QuoteC.PNG

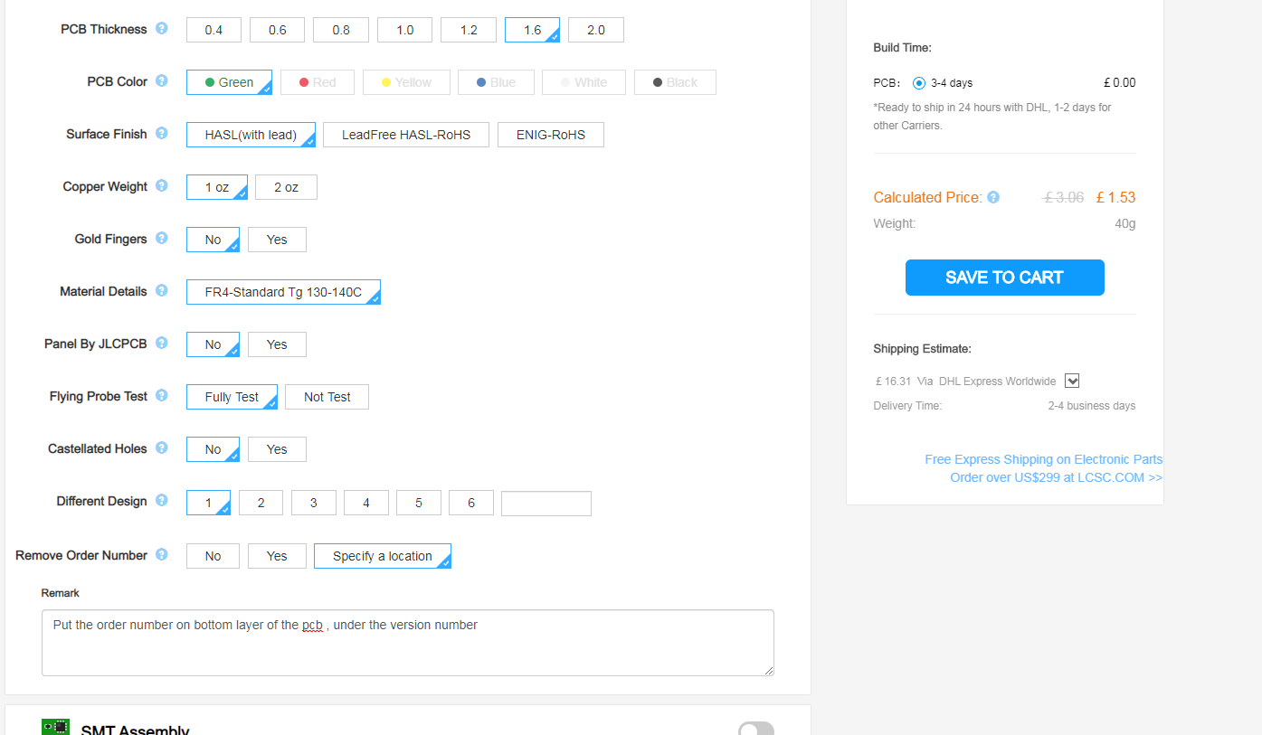
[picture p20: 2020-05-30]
Hardware/Version B2 Advance nrf52832/CAMOutputs/QuoteB.PNG

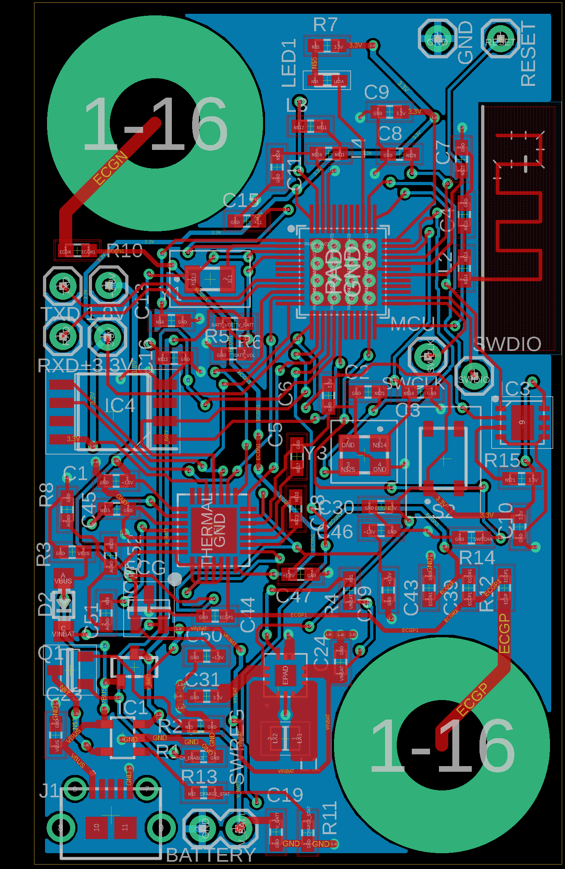
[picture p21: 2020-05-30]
Hardware/Version B2 Advance nrf52832/Layout.png

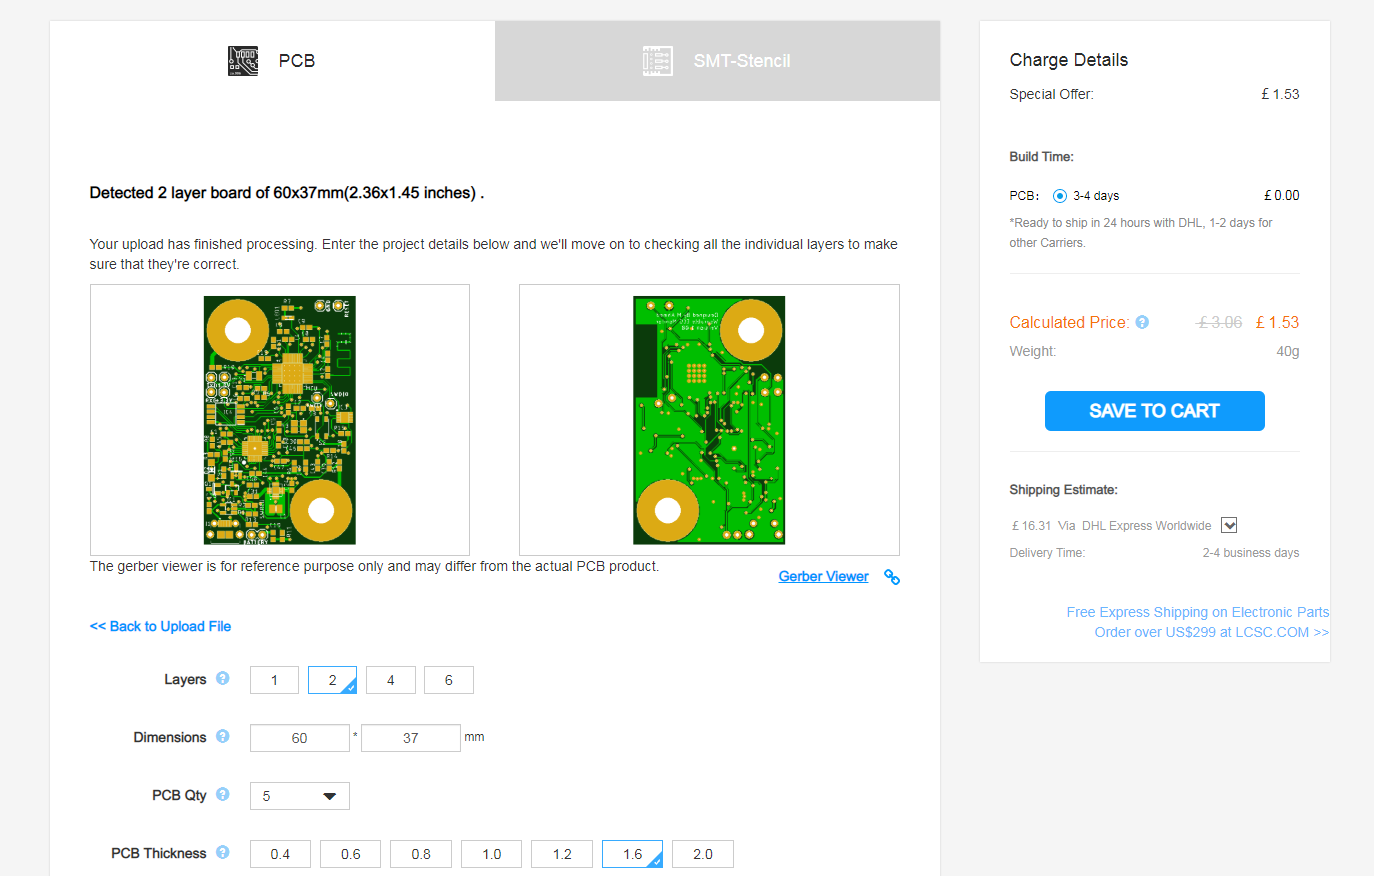
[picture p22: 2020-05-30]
Hardware/Version B1 Advance nrf52832/CAMOutputs/QuoteA.PNG

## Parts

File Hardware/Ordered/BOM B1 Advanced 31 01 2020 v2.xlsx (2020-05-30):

No. | Qty | Value | Package | Parts | Description | No. | Supplier | Order Code | Price / MOQ | MOQ | To Order Amount | Price Order | Value | Device
1 | 14 |  |  |  |  | 1 |  |  |  |  |  |  |  | RESISTOR
2 | 1 | 0R | RESC0603_N | R8 | Generic chip resistor | 2 | Farnell | 1469739 | £0.17 | 10 | 10 | £0.17 | 0R | RESISTOR_0603_N
3 | 6 | 100k | RESC0603_N | R3, R4, R5, R6, R11, R13 | Generic chip resistor | 3 | Farnell | 2447226 | £0.04 | 10 | 10 | £0.04 | 100k | RESISTOR_0603_N
4 | 3 | 10k | RESC0603_N | R1, R2, R14 | Generic chip resistor | 4 | Farnell | 2447230 | £0.04 | 10 | 10 | £0.04 | 10k | RESISTOR_0603_N
5 | 1 | 4.7k | RESC0603_N | R15 | Generic chip resistor | 5 | Farnell | 2694880 | £0.04 | 10 | 10 | £0.04 | 4.7k | RESISTOR_0603_N
6 | 2 | 49.9K | RESC0603_N | R12 | Generic chip resistor | 6 | Farnell | 2447380 | £0.05 | 10 | 10 | £0.05 | 49.9K | RESISTOR_0603_N
7 | 1 | 60R (56Ohms) | RESC0603_N | R7 | Generic chip resistor | 7 | Farnell | 2447400 | £0.05 | 10 | 10 | £0.05 | 60R (56Ohms) | RESISTOR_0603_N
8 | 29 |  |  |  |  | 8 | Farnell |  |  |  |  |  |  | CAPACITOR
9 | 1 | 0.8pF (5%) | RESC0603_N | C4 | Generic chip capacitor | 9 | Mouser | 609-251R14S0R8AV4T | £0.30 | 1 | 5 | £1.50 | 0.8pF (5%) | CAPACITOR_0603_N
10 | 4 | 100nF | RESC0603_N | C6, C9, C13, C30 | Generic chip capacitor | 10 | Farnell | 2429362 | £0.13 | 10 | 10 | £0.13 | 100nF | CAPACITOR_0603_N
11 | 1 | 100pF | RESC0603_N | C8 | Generic chip capacitor | 11 | Farnell | 2896358 | £0.18 | 10 | 10 | £0.18 | 100pF | CAPACITOR_0603_N
12 | 2 | 10pF | RESC0603_N | C43, C44 | Generic chip capacitor | 12 | Farnell | 2496879 | £0.28 | 10 | 10 | £0.28 | 10pF | CAPACITOR_0603_N
13 | 6 | 10uF | RESC0603_N | C45, C47, C50, C51,C19, C24 | Generic chip capacitor | 13 | Farnell | 2494233 | £1.33 | 10 | 10 | £1.33 | 10uF | CAPACITOR_0603_N
14 | 4 | 12pF (2%) | RESC0603_N | C2, C3, C15, C16 | Generic chip capacitor | 14 | Farnell | 2896365 | £0.67 | 10 | 10 | £0.67 | 12pF (2%) | CAPACITOR_0603_N
15 | 2 | 1nF | RESC0603_N | C5, C39 | Generic chip capacitor | 15 | Farnell | 2524816 | £0.32 | 10 | 10 | £0.32 | 1nF | CAPACITOR_0603_N
16 | 6 | 1uF | RESC0603_N | C1, C11, C46, C48, C49, C52 | Generic chip capacitor | 16 | Farnell | 9227776 | £0.32 | 10 | 10 | £0.32 | 1uF | CAPACITOR_0603_N
17 | 1 | 22µF | RESC0603_N | C31 | Generic chip capacitor | 17 | Farnell | 1845732 | £1.09 | 10 | 10 | £1.09 | 22µF | CAPACITOR_0603_N
18 | 2 | 4.7µF | RESC0603_N | C10, C23 | Generic chip capacitor | 18 | Farnell | 3013399 | £0.53 | 10 | 10 | £0.53 | 4.7µF | CAPACITOR_0603_N
19 | 4 |  |  |  |  | 19 |  |  |  |  |  |  |  | INDUCTOR
20 | 1 | 10uH (>50mA) | RESC0603_N | L3 | Generic chip inductor | 20 | Farnell | 2215650 | £0.47 | 5 | 5 | £0.47 | 10uH (>50mA) | INDUCTOR_0603_N
21 | 1 | 15nH | RESC0603_N | L4 | Generic chip inductor | 21 | Farnell | 2858912 | £0.47 | 5 | 5 | £0.47 | 15nH | INDUCTOR_0603_N
22 | 1 | 3.9nH | RESC0603_N | L2 | Generic chip inductor | 22 | Farnell | 1515389 | £1.40 | 10 | 10 | £1.40 | 3.9nH | INDUCTOR_0603_N
23 | 1 | DFE201610R-H-1R0M=P2 | INDC2016X100N | L1 | DFE201610R Series Inductor 1.0uH +/-20% 0806 (2016) | 23 | Mouser | 81-DFE201610RH1R0MP2 | £0.34 | 1 | 2 | £0.68 | DFE201610R-H-1R0M=P2 | DFE201610R-H-1R0M=P2
24 | 3 |  |  |  |  | 24 |  |  |  |  |  |  |  | DIODE
25 | 1 | IN-S63AT5G | LEDM168X39N | LED1 | Standard LEDs - SMD True Green LED | 25 | Mouser | 743-IN-S63AT5G | £0.09 | 1 | 5 | £0.45 | IN-S63AT5G | IN-S63AT5G
26 |  |  |  |  |  | 26 |  |  |  |  |  |  |  | TRANSISITORS
27 | 1 | DMG2305 | SOT23-R | Q3 | P-Channel Mosfet | 27 | Farnell | 2543532 | £1.20 | 5 | 5 | £1.20 | DMG2305 | MOSFET-P
28 | 1 | 2N7002K-7 | SOT96P240X100-3N | Q1 | N-CHANNEL ENHANCEMENT MODE MOSFET | 28 |  | 1713825 | £0.67 | 5 | 5 | £0.67 | 2N7002K-7 | 2N7002K-7
29 | 2 |  |  |  |  | 29 |  |  | £ |  |  | £ |  | CRYSTAL
30 | 1 | ABM8G-12.000MHZ-4Y-T3 | ABM8G16000MHZB4YT | Y3 | Abracon 12MHz Crystal Unit +/-30ppm SMD 4-Pin 3.2 x 2.5 x 1mm | 30 | Mouser | 815-ABM8G-106-12-T | £0.40 | 1 | 5 | £2.00 | 815-ABM8G-106-12-T | ABM8G-12.000MHZ-4Y-T3
31 | 1 | ABS07-166-32.768KHZ-T | ABS0716632768KHZT OR 449-LFXTAL009678REEL | Y1 | Crystal IOT 32.786KHz XTAL 10ppm | 31 | Mouser | 815-ABS0716632.768KT | £0.51 | 1 | 5 | £2.55 | ABS07-166-32.768KHZ-T | 32.768KHZ
32 | 8 |  |  |  |  | 32 |  |  |  |  |  |  |  | IC
33 | 1 | NRF52832 | QFN40P600X600X90-48_N | MCU | nRF52832 | 33 | Mouser | 949-NRF52832-QFAB-R | £4.13 | 1 | 3 | £12.39 | NRF52832 | NRF52832
34 | 1 | MAX30003CTI+ | QFN-28 | ECG |  | 34 | Farnell | 2668156 | £4.96 | 1 | 3 | £14.88 | MAX30003CTI+ | MAX30003
35 | 1 | MAX30205MTA+T | SON65P300X300X80-9N | IC3 | Human Body Temperature Sensor, 8 TDFN-EP | 35 | Farnell | 2668518 | £1.89 | 1 | 1 | £1.89 | MAX30205MTA+T | MAX30205MTA+T
36 | 1 | MBR120 | SOD-123 | D2 |  | 36 | Farnell | 1431041 | £0.29 | 1 | 3 | £0.29 | MBR120 | DIODE-SCHOTTKYSOD-123
37 | 1 | MCP1811AT-033_TT | SOT95P237X112-3N | IC2 | LDO Voltage Regulators Ultra Low Iq LDO | 37 | Farnell | 2990197 | £0.20 | 1 | 3 | £0.20 | MCP1811AT-033_TT | MCP1811AT-033_TT
38 | 1 | MCP73831/OT | SOT23-5L | IC1 | MCP73831/2 | 38 | Farnell | 2920755 | £0.42 | 1 | 1 | £0.42 | MCP73831/OT | MCP73831/OT
39 | 1 | AT25QF128A-SHB-T | SOIC127P790X216-8N | IC4 | NOR Flash 128Mb, 133MHz, QPI,8-SOIC-W, IND TEMP, 2.7-3.6V, T&R | 39 | Mouser | 988-AT25QF128A-SHB-T | £1.18 | 1 | 1 | £1.18 | AT25QF128A-SHB-T | AT25QF128A-SHB-T
40 | 1 | ISL9120IRTNZ | TQFN-12 | SWREG |  | 40 | Farnell | 2630543 | £1.73 | 1 | 1 | £1.73 | ISL9120IRTNZ | SWITCH REG 3.3V Fixed
41 | 2 |  |  |  |  | 41 |  |  |  |  |  |  |  | OTHER
42 | 1 | Button | PTS810SJG250SMTRLFS | S2 | IP40 Black Button Tactile Switch, SPST-NO 50 mA 3mm Surface Mount | 42 | Farnell | 3023215 | £0.96 | 10 | 10 | £0.96 | PTS810SJK250SMTRLFS | Button
43 | 1 | Micro USB | 101181940011LF | J1 | Power to the Board MICRO USD B-TYPE | 43 | Mouser | 649-10118194-0011LF | £0.31 | 1 | NULL | £0.00 | 10118194-0011LF | Micro USB
44 |  |  |  |  |  | 44 |  |  | £27.16 |  |  | £50.57

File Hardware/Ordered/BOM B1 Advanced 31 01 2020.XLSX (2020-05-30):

Qty | Value | Package | Parts | Description | Supplier | Order Code | Price / MOQ | MOQ | To Order Amount | Price Order | Value | Device
14 |  |  |  |  |  |  |  |  |  |  |  | RESISTOR
1 | 0R | RESC0603_N | R8 | Generic chip resistor | Farnell | 1469739 | £0.17 | 10 | 10 | £0.17 | 0R | RESISTOR_0603_N
6 | 100k | RESC0603_N | R3, R4, R5, R6, R11, R13 | Generic chip resistor | Farnell | 2447226 | £0.04 | 10 | 10 | £0.04 | 100k | RESISTOR_0603_N
3 | 10k | RESC0603_N | R1, R2, R14 | Generic chip resistor | Farnell | 2447230 | £0.04 | 10 | 10 | £0.04 | 10k | RESISTOR_0603_N
1 | 4.7k | RESC0603_N | R15 | Generic chip resistor | Farnell | 2694880 | £0.04 | 10 | 10 | £0.04 | 4.7k | RESISTOR_0603_N
2 | 49.9K | RESC0603_N | R12 | Generic chip resistor | Farnell | 2447380 | £0.05 | 10 | 10 | £0.05 | 49.9K | RESISTOR_0603_N
1 | 60R (56Ohms) | RESC0603_N | R7 | Generic chip resistor | Farnell | 2447400 | £0.05 | 10 | 10 | £0.05 | 60R (56Ohms) | RESISTOR_0603_N
29 |  |  |  |  | Farnell |  |  |  |  |  |  | CAPACITOR
1 | 0.8pF (5%) | RESC0603_N | C4 | Generic chip capacitor | Mouser | 609-251R14S0R8AV4T | £0.30 | 1 | 5 | £1.50 | 0.8pF (5%) | CAPACITOR_0603_N
4 | 100nF | RESC0603_N | C6, C9, C13, C30 | Generic chip capacitor | Farnell | 2429362 | £0.13 | 10 | 10 | £0.13 | 100nF | CAPACITOR_0603_N
1 | 100pF | RESC0603_N | C8 | Generic chip capacitor | Farnell | 2896358 | £0.18 | 10 | 10 | £0.18 | 100pF | CAPACITOR_0603_N
2 | 10pF | RESC0603_N | C43, C44 | Generic chip capacitor | Farnell | 2496879 | £0.28 | 10 | 10 | £0.28 | 10pF | CAPACITOR_0603_N
6 | 10uF | RESC0603_N | C45, C47, C50, C51,C19, C24 | Generic chip capacitor | Farnell | 2494233 | £1.33 | 10 | 10 | £1.33 | 10uF | CAPACITOR_0603_N
4 | 12pF (2%) | RESC0603_N | C2, C3, C15, C16 | Generic chip capacitor | Farnell | 2896365 | £0.67 | 10 | 10 | £0.67 | 12pF (2%) | CAPACITOR_0603_N
2 | 1nF | RESC0603_N | C5, C39 | Generic chip capacitor | Farnell | 2524816 | £0.32 | 10 | 10 | £0.32 | 1nF | CAPACITOR_0603_N
6 | 1uF | RESC0603_N | C1, C11, C46, C48, C49, C52 | Generic chip capacitor | Farnell | 9227776 | £0.32 | 10 | 10 | £0.32 | 1uF | CAPACITOR_0603_N
1 | 22µF | RESC0603_N | C31 | Generic chip capacitor | Farnell | 1845732 | £1.09 | 10 | 10 | £1.09 | 22µF | CAPACITOR_0603_N
2 | 4.7µF | RESC0603_N | C10, C23 | Generic chip capacitor | Farnell | 3013399 | £0.53 | 10 | 10 | £0.53 | 4.7µF | CAPACITOR_0603_N
4 |  |  |  |  |  |  |  |  |  |  |  | INDUCTOR
1 | 10uH (>50mA) | RESC0603_N | L3 | Generic chip inductor | Farnell | 2215650 | £0.47 | 5 | 5 | £0.47 | 10uH (>50mA) | INDUCTOR_0603_N
1 | 15nH | RESC0603_N | L4 | Generic chip inductor | Farnell | 2858912 | £0.47 | 5 | 5 | £0.47 | 15nH | INDUCTOR_0603_N
1 | 3.9nH | RESC0603_N | L2 | Generic chip inductor | Farnell | 1515389 | £1.40 | 10 | 10 | £1.40 | 3.9nH | INDUCTOR_0603_N
1 | DFE201610R-H-1R0M=P2 | INDC2016X100N | L1 | DFE201610R Series Inductor 1.0uH +/-20% 0806 (2016) | Mouser | 81-DFE201610RH1R0MP2 | £0.34 | 1 | 2 | £0.68 | DFE201610R-H-1R0M=P2 | DFE201610R-H-1R0M=P2
3 |  |  |  |  |  |  |  |  |  |  |  | DIODE
1 | IN-S63AT5G | LEDM168X39N | LED1 | Standard LEDs - SMD True Green LED | Mouser | 743-IN-S63AT5G | £0.09 | 1 | 5 | £0.45 | IN-S63AT5G | IN-S63AT5G
 |  |  |  |  |  |  |  |  |  |  |  | TRANSISITORS
1 | DMG2305 | SOT23-R | Q3 | P-Channel Mosfet | Farnell | 2543532 | £1.20 | 5 | 5 | £1.20 | DMG2305 | MOSFET-P
1 | 2N7002K-7 | SOT96P240X100-3N | Q1 | N-CHANNEL ENHANCEMENT MODE MOSFET |  | 1713825 | £0.67 | 5 | 5 | £0.67 | 2N7002K-7 | 2N7002K-7
2 |  |  |  |  |  |  | £ |  |  | £ |  | CRYSTAL
1 | ABM8G-12.000MHZ-4Y-T3 | ABM8G16000MHZB4YT | Y3 | Abracon 12MHz Crystal Unit +/-30ppm SMD 4-Pin 3.2 x 2.5 x 1mm | Mouser | 815-ABM8G-106-12-T | £0.40 | 1 | 5 | £2.00 | 815-ABM8G-106-12-T | ABM8G-12.000MHZ-4Y-T3
1 | ABS07-166-32.768KHZ-T | ABS0716632768KHZT OR 449-LFXTAL009678REEL | Y1 | Crystal IOT 32.786KHz XTAL 10ppm | Mouser | 815-ABS0716632.768KT | £0.51 | 1 | 5 | £2.55 | ABS07-166-32.768KHZ-T | 32.768KHZ
8 |  |  |  |  |  |  |  |  |  |  |  | IC
1 | NRF52832 | QFN40P600X600X90-48_N | MCU | nRF52832 | Mouser | 949-NRF52832-QFAB-R | £4.13 | 1 | 3 | £12.39 | NRF52832 | NRF52832
1 | MAX30003CTI+ | QFN-28 | ECG |  | Farnell | 2668156 | £4.96 | 1 | 3 | £14.88 | MAX30003CTI+ | MAX30003
1 | MAX30205MTA+T | SON65P300X300X80-9N | IC3 | Human Body Temperature Sensor, 8 TDFN-EP | Farnell | 2668518 | £1.89 | 1 | 1 | £1.89 | MAX30205MTA+T | MAX30205MTA+T
1 | MBR120 | SOD-123 | D2 |  | Farnell | 1431041 | £0.29 | 1 | 3 | £0.29 | MBR120 | DIODE-SCHOTTKYSOD-123
1 | MCP1811AT-033_TT | SOT95P237X112-3N | IC2 | LDO Voltage Regulators Ultra Low Iq LDO | Farnell | 2990197 | £0.20 | 1 | 3 | £0.20 | MCP1811AT-033_TT | MCP1811AT-033_TT
1 | MCP73831/OT | SOT23-5L | IC1 | MCP73831/2 | Farnell | 2920755 | £0.42 | 1 | 1 | £0.42 | MCP73831/OT | MCP73831/OT
1 | AT25QF128A-SHB-T | SOIC127P790X216-8N | IC4 | NOR Flash 128Mb, 133MHz, QPI,8-SOIC-W, IND TEMP, 2.7-3.6V, T&R | Mouser | 988-AT25QF128A-SHB-T | £1.18 | 1 | 1 | £1.18 | AT25QF128A-SHB-T | AT25QF128A-SHB-T
1 | ISL9120IRTNZ | TQFN-12 | SWREG |  | Farnell | 2630543 | £1.73 | 1 | 1 | £1.73 | ISL9120IRTNZ | SWITCH REG 3.3V Fixed
2 |  |  |  |  |  |  |  |  |  |  |  | OTHER
1 | Button | PTS810SJG250SMTRLFS | S2 | IP40 Black Button Tactile Switch, SPST-NO 50 mA 3mm Surface Mount | Farnell | 3023215 | £0.96 | 10 | 10 | £0.96 | PTS810SJK250SMTRLFS | Button
1 | Micro USB | 101181940011LF | J1 | Power to the Board MICRO USD B-TYPE | Mouser | 649-10118194-0011LF | £0.31 | 1 | NULL | £0.00 | 10118194-0011LF | Micro USB
 |  |  |  |  |  |  | £27.16 |  |  | £50.57

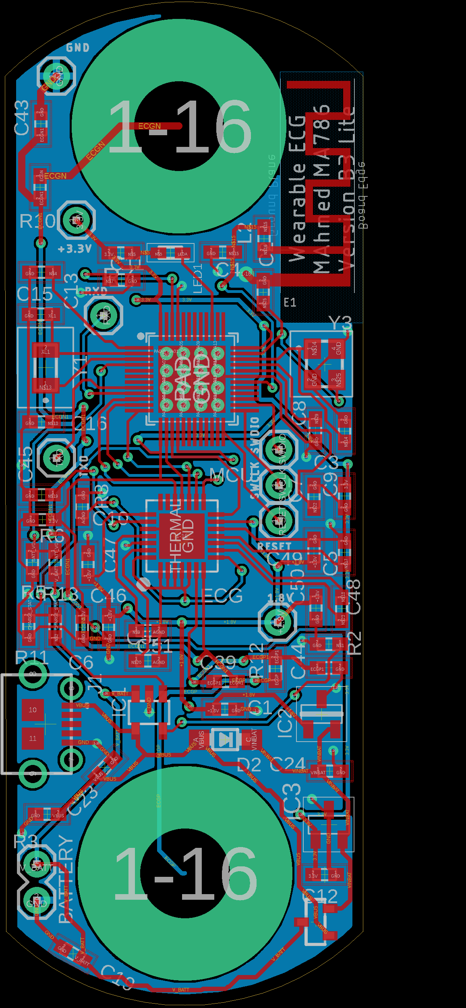
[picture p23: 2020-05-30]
Hardware/Ordered/Version B3 Lite nrf52832/lay.png

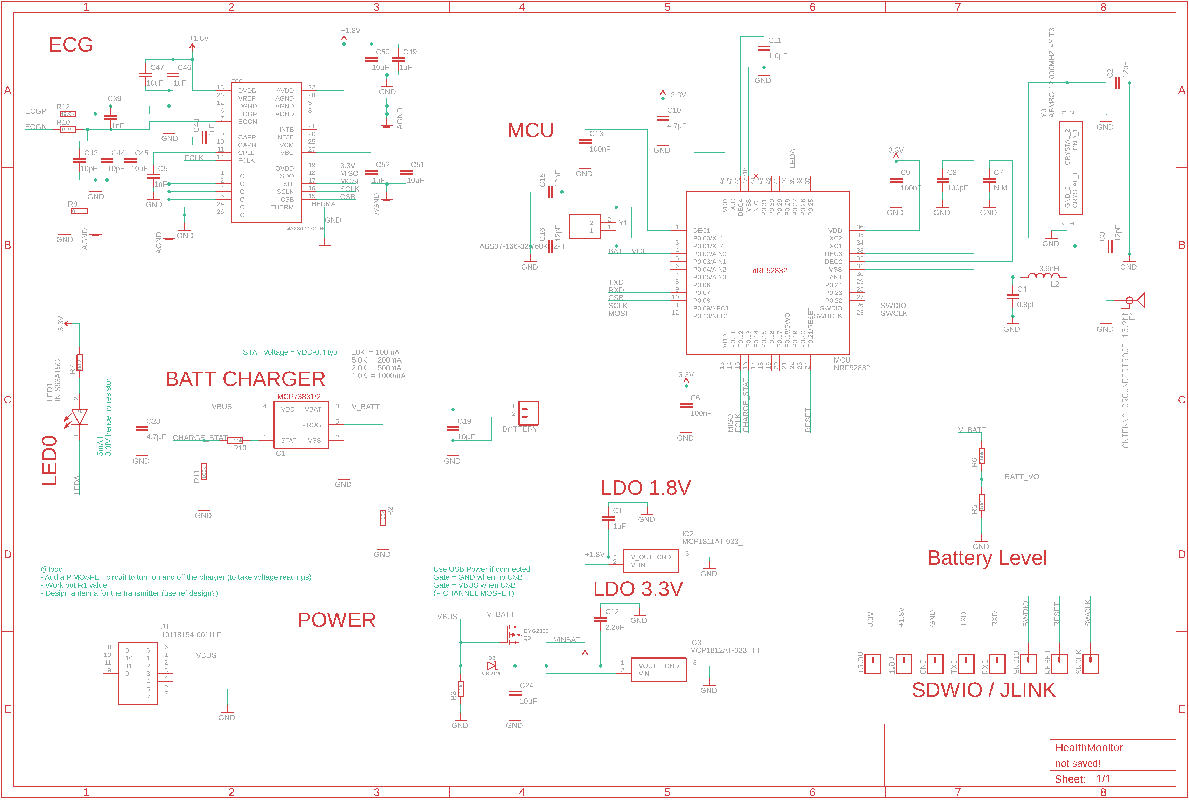
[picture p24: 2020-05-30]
Hardware/Ordered/Version B3 Lite nrf52832/Sch.png

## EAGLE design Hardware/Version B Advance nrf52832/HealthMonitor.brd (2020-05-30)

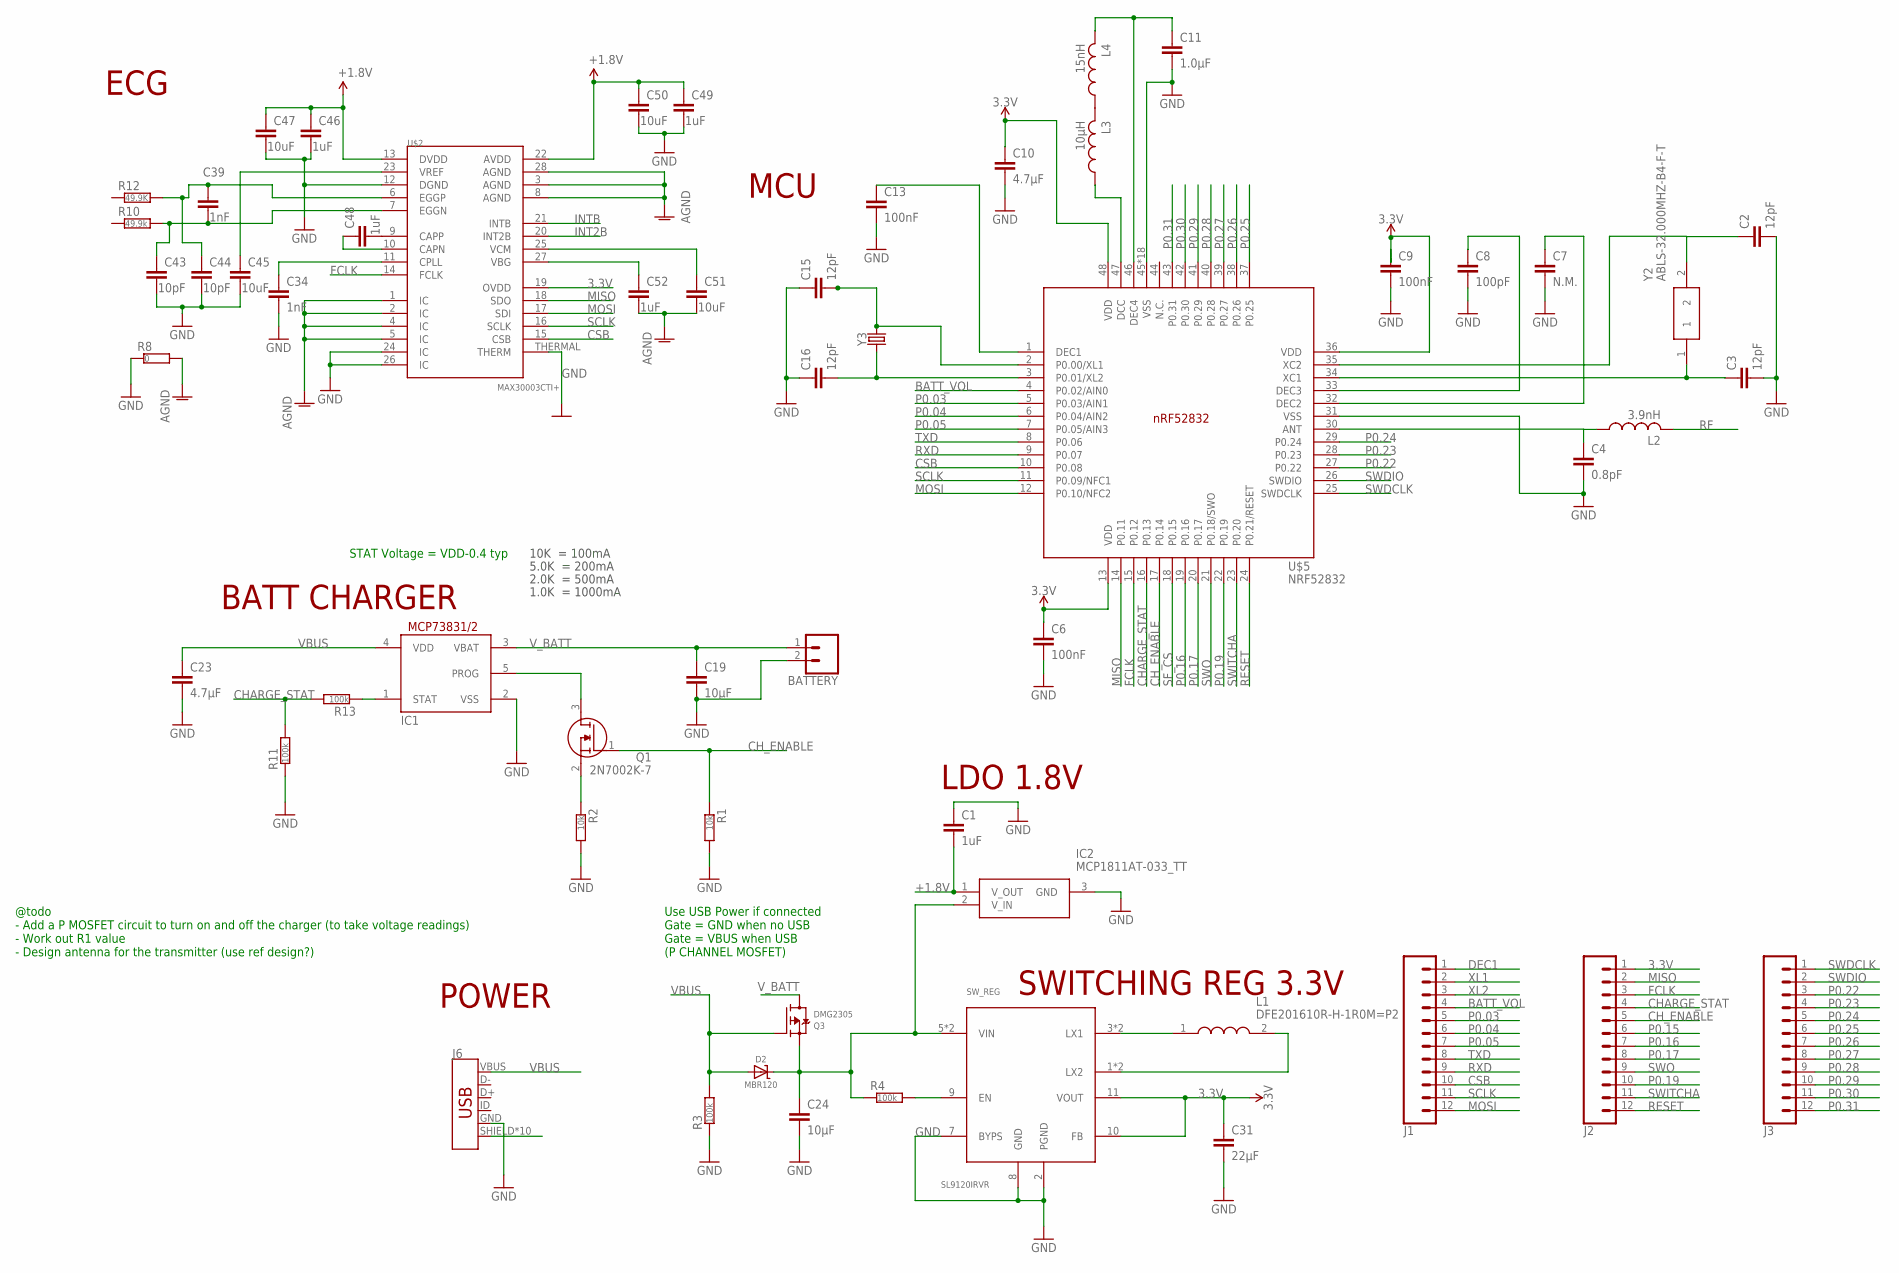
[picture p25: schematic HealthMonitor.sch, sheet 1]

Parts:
BATTERY: CONN_02; 1X02
C1: 1uF; RESC0603_L
C2, C3, C15, C16: 12pF; RESC0603_L
C4: 0.8pF; RESC0603_L
C6, C9, C13: 100nF; RESC0603_L
C7: N.M.; RESC0603_L
C8: 100pF; RESC0603_L
C10, C23: 4.7µF; RESC0603_N
C11: 1.0µF; RESC0603_N
C19, C24: 10µF; RESC0603_N
C31: 22µF; RESC0603_N
C34: 1nF; C0603
C39: 1nF; RESC0603_N
C43, C44: 10pF; RESC0603_N
C45, C47, C50, C51: 10uF; RESC0603_N
C46, C48, C49, C52: 1uF; RESC0603_N
D2: MBR120; SOD-123
IC1: MCP73831/OT; SOT23-5L
IC2: MCP1811AT-033_TT; SOT95P237X112-3N
J1, J2, J3: CONN_12; 1X12
J6: USB_MICRO-B_HALF_PTH_MILL; USB-MICROB-PTH-MILL
L1: DFE201610R-H-1R0M=P2; INDC2016X100N
L2: 3.9nH; RESC0402_N
L3: 10µH; RESC0603_N
L4: 15nH; RESC0402_N
Q1: 2N7002K-7; SOT96P240X100-3N
Q3: DMG2305; SOT23-R
R1, R2: 10k; RESC0603_L
R3, R4, R11, R13: 100k; RESC0603_L
R8: 0; RESC0603_L
R10: 49.9k; RESC0603_L
R12: 49.9K; RESC0603_L
SW_REG: SL9120IRVR; TQFN-12
U$2: MAX30003CTI+; QFN-28
U$5: NRF52832; QFN40P600X600X90-48_N
Y2: ABLS-32.000MHZ-B4-F-T; ABLS-12.000MHZ-B2
Y3: CRYSTALSMD-2X6; CRYSTAL-SMD-2X6-CYL

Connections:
3.3V: C6.1, C9.1, C10.1, C31.1, J2.1, SW_REG.10 (FB), SW_REG.11 (VOUT), U$2.19 (OVDD), U$5.13 (VDD), U$5.36 (VDD), U$5.48 (VDD); also elsewhere on the board
+1.8V: C1.2, C46.1, C47.1, C49.1, C50.1, IC2.1 (V_OUT), U$2.13 (DVDD), U$2.22 (AVDD); also elsewhere on the board
AGND: C51.2, C52.2, R8.2, U$2.1 (IC), U$2.2 (IC), U$2.3 (AGND), U$2.4 (IC), U$2.5 (IC), U$2.8 (AGND), U$2.28 (AGND)
BATT_VOL: J1.4, U$5.4 (P0.02/AIN0); also elsewhere on the board
CHARGE_STAT: J2.4, R11.2, R13.2, U$5.16 (P0.13)
CH_ENABLE: J2.5, Q1.1 (G), R1.1, U$5.17 (P0.14)
CSB: J1.10, U$2.15 (CSB), U$5.10 (P0.08)
DEC1: J1.1
ECGN1: C39.2, C43.1, R10.2, U$2.7 (EGGN)
ECGP1: C39.1, C44.1, R12.2, U$2.6 (EGGP)
FCLK: J2.3, U$2.14 (FCLK), U$5.15 (P0.12)
GND: BATTERY.2, C1.1, C2.2, C3.2, C4.2, C6.2, C7.2, C8.2, C9.2, C10.2, C11.2, C13.2, C15.1, C16.1, C19.2, C23.2, C24.2, C31.2, C34.2, C43.2, C44.2, C45.2, C46.2, C47.2, C49.2, C50.2, IC1.2 (VSS), IC2.3 (GND), J6.GND, R1.2, R2.2, R3.1, R8.1, R11.1, SW_REG.2 (PGND), SW_REG.7 (BYPS), SW_REG.8 (GND), U$2.12 (DGND), U$2.24 (IC), U$2.26 (IC), U$2.THERMAL (THERM), U$5.31 (VSS), U$5.45 (VSS), U$5.PAD (VSS), U$5.PAD@VIA01 (VSS), U$5.PAD@VIA02 (VSS), U$5.PAD@VIA03 (VSS), U$5.PAD@VIA04 (VSS), U$5.PAD@VIA05 (VSS), U$5.PAD@VIA06 (VSS), U$5.PAD@VIA07 (VSS), U$5.PAD@VIA08 (VSS), U$5.PAD@VIA09 (VSS), U$5.PAD@VIA10 (VSS), U$5.PAD@VIA11 (VSS), U$5.PAD@VIA12 (VSS), U$5.PAD@VIA13 (VSS), U$5.PAD@VIA14 (VSS), U$5.PAD@VIA15 (VSS), U$5.PAD@VIA16 (VSS); also elsewhere on the board
INT2B: U$2.20 (INT2B)
INTB: U$2.21 (INTB)
MISO: J2.2, U$2.18 (SDO), U$5.14 (P0.11); also elsewhere on the board
MOSI: J1.12, U$2.17 (SDI), U$5.12 (P0.10/NFC2); also elsewhere on the board
unnamed: R4.2, SW_REG.9 (EN)
unnamed: IC1.1 (STAT), R13.1
unnamed: Q1.2 (S), R2.1
unnamed: C13.1, U$5.1 (DEC1)
unnamed: L1.1, SW_REG.3 (LX1), SW_REG.4 (LX1)
unnamed: C24.1, D2.C, IC2.2 (V_IN), Q3.2 (S), R4.1, SW_REG.5 (VIN), SW_REG.6 (VIN)
unnamed: IC1.5 (PROG), Q1.3 (D)
unnamed: L1.2, SW_REG.1 (LX2), SW_REG.12 (LX2)
unnamed: C51.1, U$2.25 (VCM)
unnamed: C2.1, Y2.2
unnamed: L3.2, L4.1
unnamed: L3.1, U$5.47 (DCC)
unnamed: C16.2, U$5.3 (P0.01/XL2), Y3.X1 (1)
unnamed: C3.1, U$5.34 (XC1), Y2.1
unnamed: C4.1, L2.1
unnamed: C34.1, U$2.11 (CPLL)
unnamed: C48.1, U$2.10 (CAPN)
unnamed: C45.1, U$2.23 (VREF)
unnamed: C52.1, U$2.27 (VBG)
unnamed: C7.1, U$5.32 (DEC2)
unnamed: C48.2, U$2.9 (CAPP)
unnamed: C11.1, L4.2, U$5.46 (DEC4)
unnamed: C8.1, U$5.33 (DEC3)
P0.03: J1.5, U$5.5 (P0.03/AIN1)
P0.04: J1.6, U$5.6 (P0.04/AIN2)
P0.05: J1.7, U$5.7 (P0.05/AIN3)
P0.15: J2.6
P0.16: J2.7, U$5.19 (P0.16)
P0.17: J2.8, U$5.20 (P0.17)
P0.19: J2.10, U$5.22 (P0.19)
P0.22: J3.3, U$5.27 (P0.22)
P0.23: J3.4, U$5.28 (P0.23)
P0.24: J3.5, U$5.29 (P0.24)
P0.25: J3.6, U$5.37 (P0.25)
P0.26: J3.7, U$5.38 (P0.26)
P0.27: J3.8, U$5.39 (P0.27)
P0.28: J3.9, U$5.40 (P0.28)
P0.29: J3.10, U$5.41 (P0.29)
P0.30: J3.11, U$5.42 (P0.30)
P0.31: J3.12, U$5.43 (P0.31)
RESET: J2.12, U$5.24 (P0.21/RESET); also elsewhere on the board
RF: L2.2
RXD: J1.9, U$5.9 (P0.07); also elsewhere on the board
SCLK: J1.11, U$2.16 (SCLK), U$5.11 (P0.09/NFC1); also elsewhere on the board
SF_CS: U$5.18 (P0.15); also elsewhere on the board
SHIELD: J6.SHIELD, J6.SHIELD2 (SHIELD), J6.SHIELD3 (SHIELD), J6.SHIELD4 (SHIELD), J6.SHIELD5 (SHIELD), J6.SHIELD6 (SHIELD), J6.SHIELD7 (SHIELD), J6.SHIELD8 (SHIELD), J6.SHIELD9 (SHIELD), J6.SHIELD10 (SHIELD)
SWDCLK: J3.1, U$5.25 (SWDCLK)
SWDIO: J3.2, U$5.26 (SWDIO); also elsewhere on the board
SWITCHA: J2.11, U$5.23 (P0.20); also elsewhere on the board
SWO: J2.9, U$5.21 (P0.18/SWO)
TXD: J1.8, U$5.8 (P0.06); also elsewhere on the board
VBUS: C23.1, D2.A, IC1.4 (VDD), J6.VBUS, Q3.1 (G), R3.2
V_BATT: BATTERY.1, C19.1, IC1.3 (VBAT), Q3.3 (D); also elsewhere on the board
XL1: C15.2, J1.2, U$5.2 (P0.00/XL1), Y3.X2 (2)
XL2: J1.3

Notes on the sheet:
10K = 100mA
5.0K = 200mA
2.0K = 500mA
1.0K = 1000mA
Use USB Power if connected Gate = GND when no USB Gate = VBUS when USB (P CHANNEL MOSFET)
ECG
STAT Voltage = VDD-0.4 typ
@todo - Add a P MOSFET circuit to turn on and off the charger (to take voltage readings) - Work out R1 value - Design antenna for the transmitter (use ref design?)
POWER
BATT CHARGER
LDO 1.8V
SWITCHING REG 3.3V
MCU

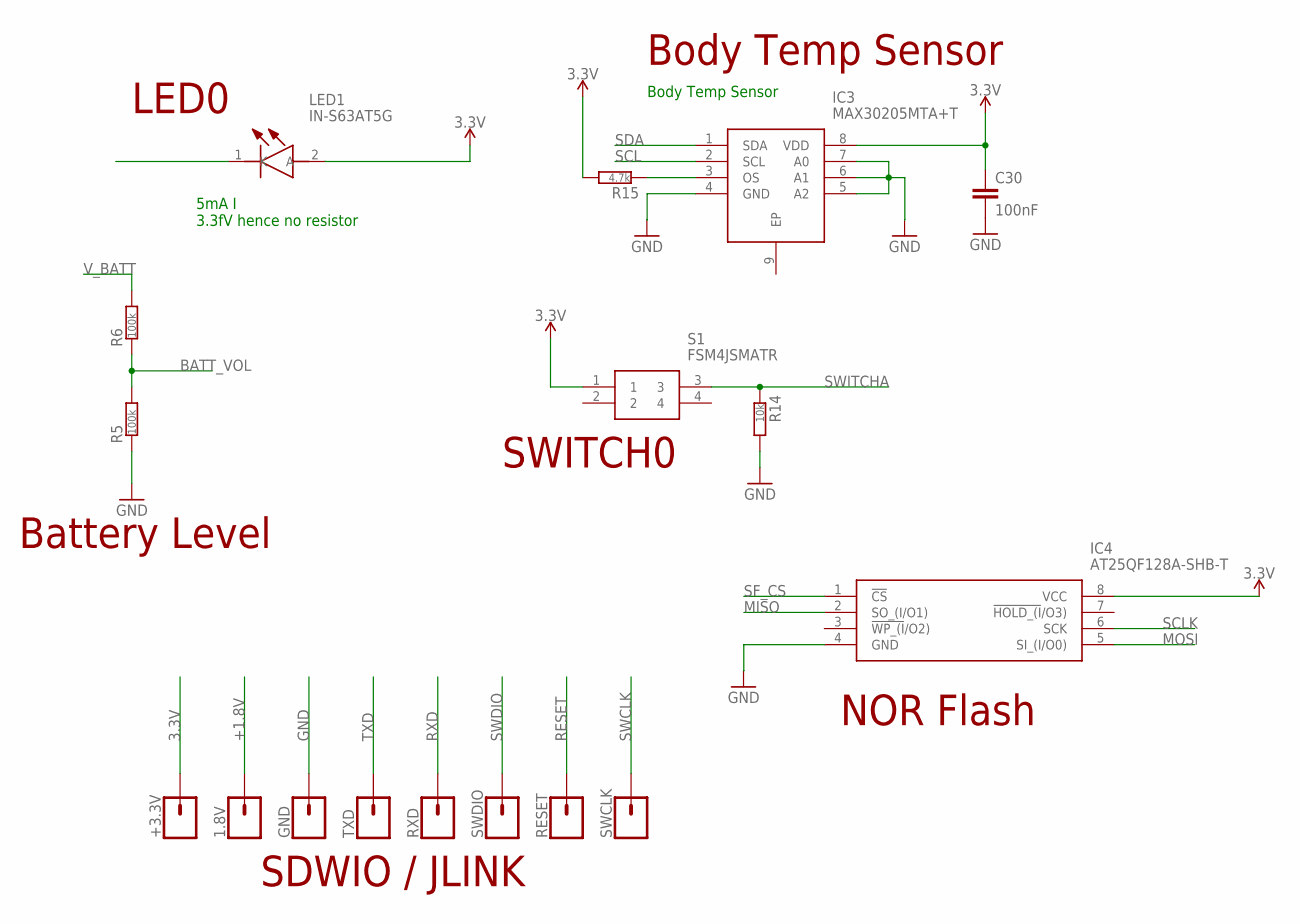
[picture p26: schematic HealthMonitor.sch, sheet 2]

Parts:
1.8V: CONN_01; 1X01
+3.3V: CONN_01; 1X01
C30: 100nF; RESC0603_L
GND: CONN_01; 1X01
IC3: MAX30205MTA+T; SON65P300X300X80-9N
IC4: AT25QF128A-SHB-T; SOIC127P790X216-8N
LED1: IN-S63AT5G; LEDM168X39N
R5, R6: 100k; RESC0603_L
R14: 10k; RESC0603_L
R15: 4.7k; RESC0603_L
RESET: CONN_01; 1X01
RXD: CONN_01; 1X01
S1: FSM4JSMATR
SWCLK: CONN_01; 1X01
SWDIO: CONN_01; 1X01
TXD: CONN_01; 1X01

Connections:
3.3V: +3.3V.1, C30.1, IC3.8 (VDD), IC4.8 (VCC), LED1.2 (A), R15.2, S1.1; also elsewhere on the board
+1.8V: 1.8V.1; also elsewhere on the board
BATT_VOL: R5.2, R6.1; also elsewhere on the board
GND: C30.2, GND.1, IC3.4 (GND), IC3.5 (A2), IC3.6 (A1), IC3.7 (A0), IC4.4 (GND), R5.1, R14.2; also elsewhere on the board
LEDA: LED1.1 (K)
MISO: IC4.2 (SO_(I/O1)); also elsewhere on the board
MOSI: IC4.5 (SI_(I/O0)); also elsewhere on the board
unnamed: IC3.3 (OS), R15.1
RESET: RESET.1; also elsewhere on the board
RXD: RXD.1; also elsewhere on the board
SCL: IC3.2 (SCL)
SCLK: IC4.6 (SCK); also elsewhere on the board
SDA: IC3.1 (SDA)
SF_CS: IC4.1 (!CS); also elsewhere on the board
SWCLK: SWCLK.1
SWDIO: SWDIO.1; also elsewhere on the board
SWITCHA: R14.1, S1.3; also elsewhere on the board
TXD: TXD.1; also elsewhere on the board
V_BATT: R6.2; also elsewhere on the board

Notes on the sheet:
Body Temp Sensor
5mA I 3.3fV hence no resistor
Battery Level
LED0
SWITCH0
Body Temp Sensor
NOR Flash
SDWIO / JLINK

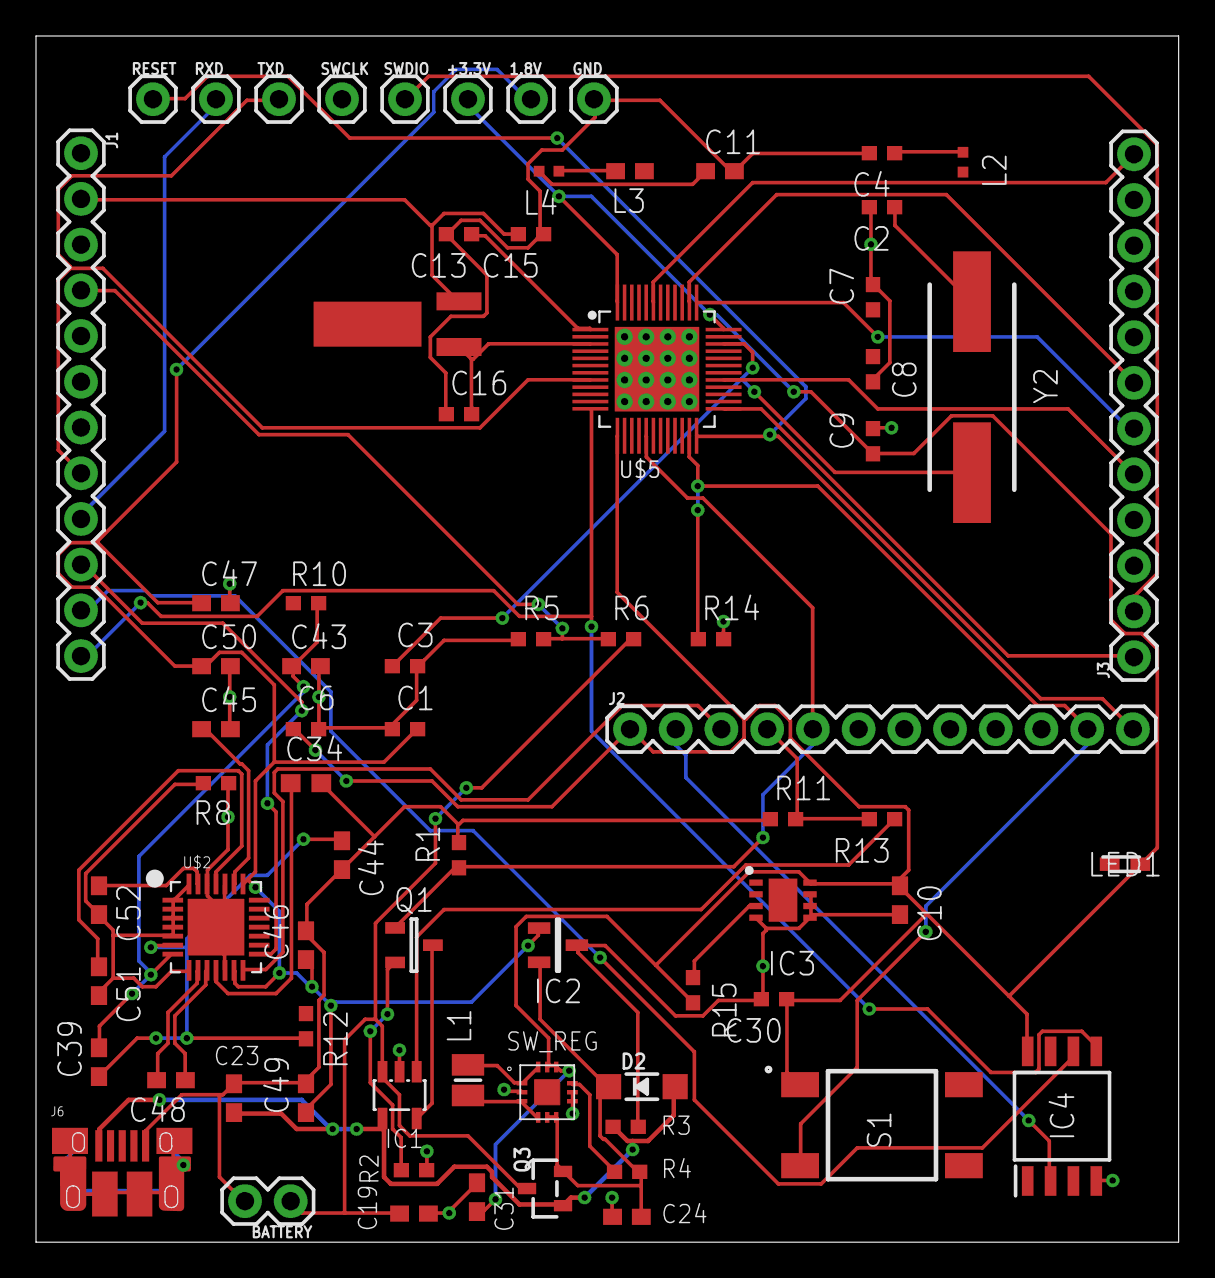
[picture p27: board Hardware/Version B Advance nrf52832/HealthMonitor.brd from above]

Board: 2 copper layers, 63.5 x 67.0 mm, 74 parts (0 on the bottom side), 66 nets.

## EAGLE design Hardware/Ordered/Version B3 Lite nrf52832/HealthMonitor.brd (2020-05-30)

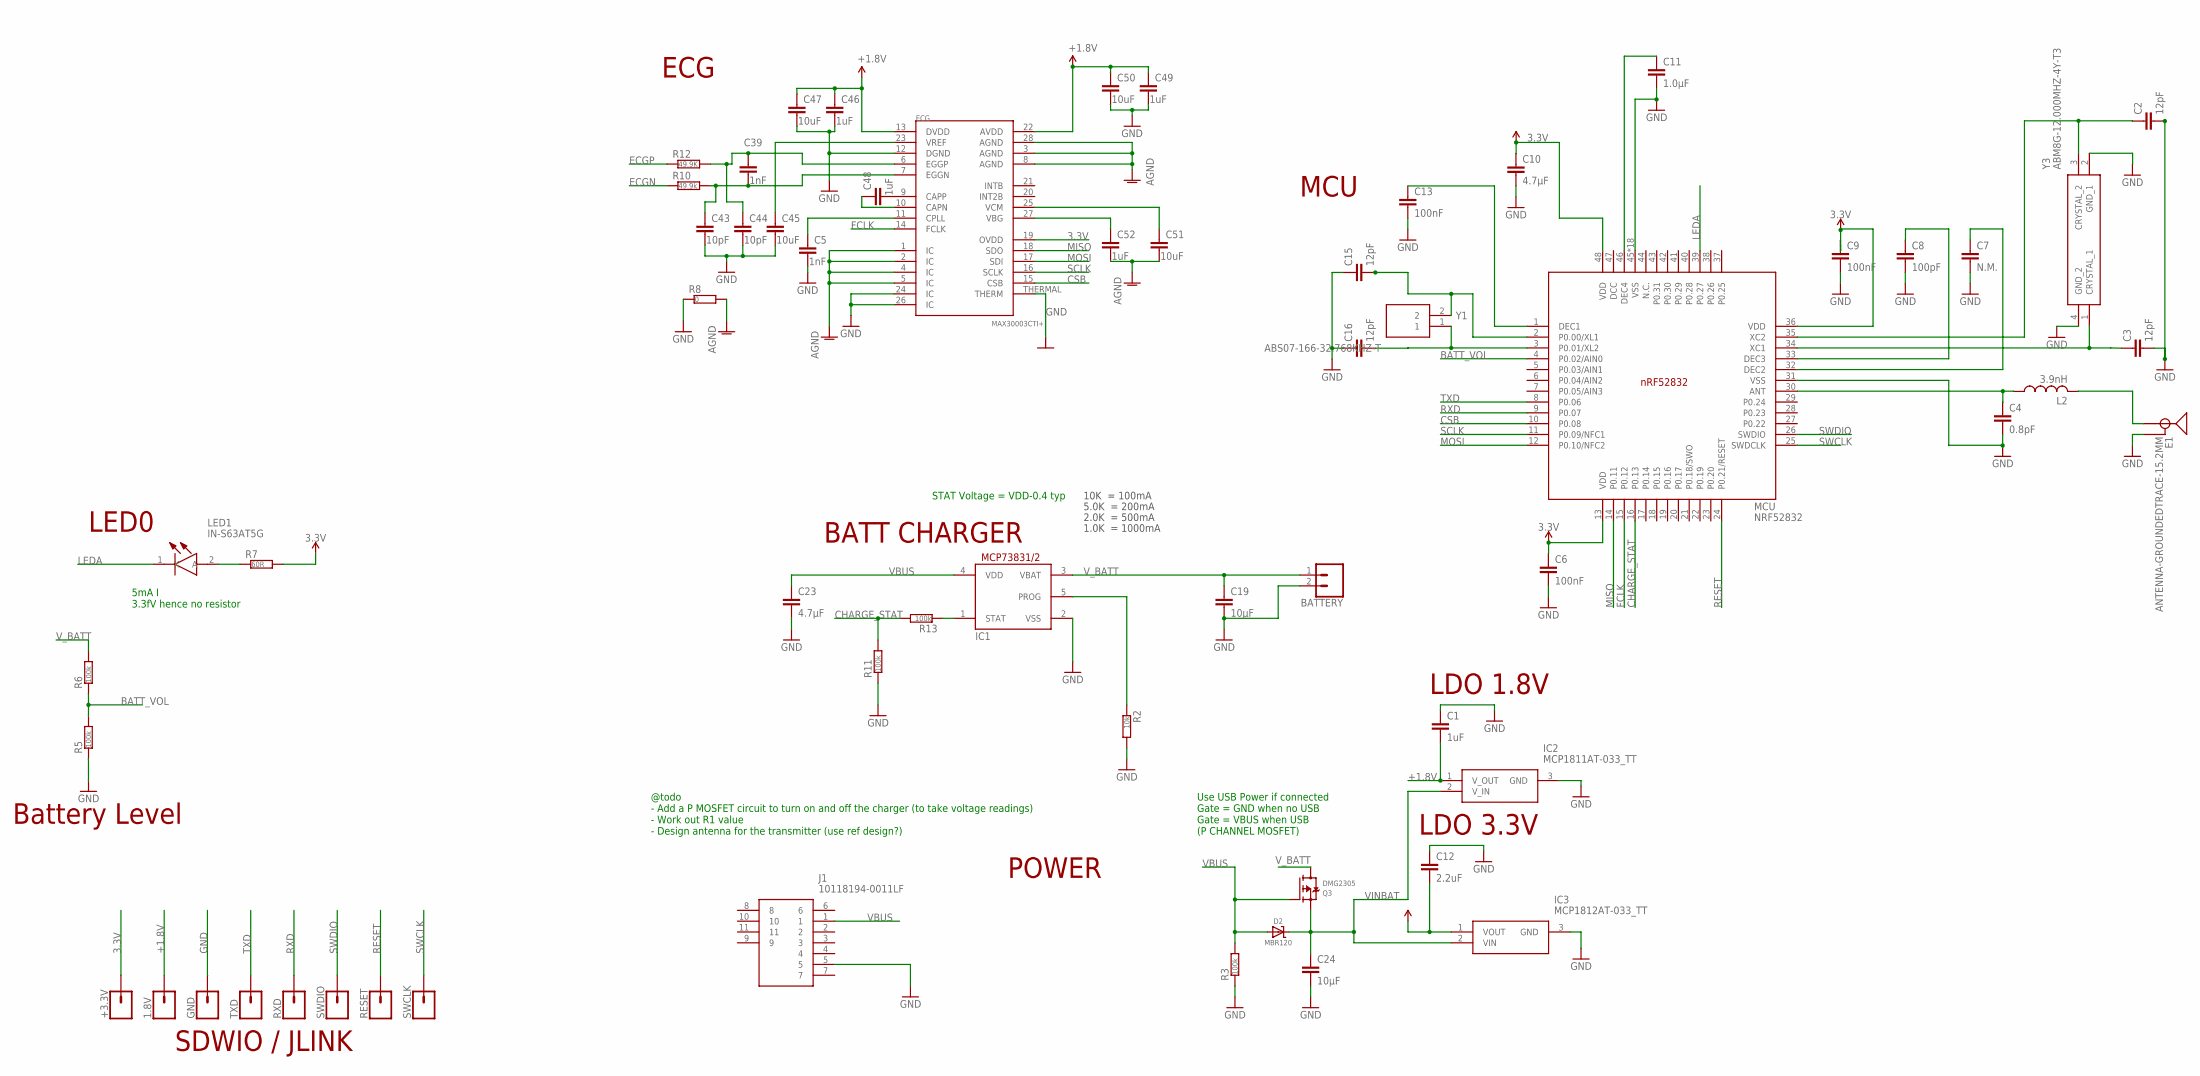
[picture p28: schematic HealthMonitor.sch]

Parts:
1.8V: CONN_01; 1X01
+3.3V: CONN_01; 1X01
BATTERY: CONN_02; 1X02
C1, C46, C48, C49, C52: 1uF; RESC0603_N
C2, C3, C15, C16: 12pF; RESC0603_N
C4: 0.8pF; RESC0603_N
C5, C39: 1nF; RESC0603_N
C6, C9, C13: 100nF; RESC0603_N
C7: N.M.; RESC0603_N
C8: 100pF; RESC0603_N
C10, C23: 4.7µF; RESC0603_N
C11: 1.0µF; RESC0603_N
C12: 2.2uF; RESC0603_N
C19, C24: 10µF; RESC0603_N
C43, C44: 10pF; RESC0603_N
C45, C47, C50, C51: 10uF; RESC0603_N
D2: MBR120; SOD-123
E1: ANTENNA-GROUNDEDTRACE-15.2MM; TRACE_ANTENNA_2.4GHZ_15.2MM
ECG: MAX30003CTI+; QFN-28
GND: CONN_01; 1X01
IC1: MCP73831/OT; SOT23-5L
IC2: MCP1811AT-033_TT; SOT95P237X112-3N@1
IC3: MCP1812AT-033_TT; SOT95P237X112-3N
J1: 10118194-0011LF; 101181940011LF
L2: 3.9nH; RESC0603_N
LED1: IN-S63AT5G; LEDM168X39N
MCU: NRF52832; QFN40P600X600X90-48_N
Q3: DMG2305; SOT23-R
R2: 10k; RESC0603_N
R3, R5, R6, R11, R13: 100k; RESC0603_N
R7: 60R; RESC0603_N
R8: 0; RESC0603_N
R10: 49.9k; RESC0603_N
R12: 49.9K; RESC0603_N
RESET: CONN_01; 1X01
RXD: CONN_01; 1X01
SWCLK: CONN_01; 1X01
SWDIO: CONN_01; 1X01
TXD: CONN_01; 1X01
Y1: ABS07-166-32.768KHZ-T; ABS0716632768KHZT
Y3: ABM8G-12.000MHZ-4Y-T3; ABM8G16000MHZB4YT

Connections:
3.3V: +3.3V.1, C6.1, C9.1, C10.1, C12.2, ECG.19 (OVDD), IC3.1 (VOUT), MCU.13 (VDD), MCU.36 (VDD), MCU.48 (VDD), R7.2
+1.8V: 1.8V.1, C1.2, C46.1, C47.1, C49.1, C50.1, ECG.13 (DVDD), ECG.22 (AVDD), IC2.1 (V_OUT)
AGND: C51.2, C52.2, ECG.1 (IC), ECG.2 (IC), ECG.3 (AGND), ECG.4 (IC), ECG.5 (IC), ECG.8 (AGND), ECG.28 (AGND), R8.2
BATT_VOL: MCU.4 (P0.02/AIN0), R5.2, R6.1
CHARGE_STAT: MCU.16 (P0.13), R11.2, R13.2
CSB: ECG.15 (CSB), MCU.10 (P0.08)
ECGN: R10.1
ECGN1: C39.2, C43.1, ECG.7 (EGGN), R10.2
ECGP: R12.1
ECGP1: C39.1, C44.1, ECG.6 (EGGP), R12.2
FCLK: ECG.14 (FCLK), MCU.15 (P0.12)
GND: BATTERY.2, C1.1, C2.2, C3.2, C4.2, C5.2, C6.2, C7.2, C8.2, C9.2, C10.2, C11.2, C12.1, C13.2, C15.1, C16.1, C19.2, C23.2, C24.2, C43.2, C44.2, C45.2, C46.2, C47.2, C49.2, C50.2, E1.GND, ECG.12 (DGND), ECG.24 (IC), ECG.26 (IC), ECG.THERMAL (THERM), GND.1, IC1.2 (VSS), IC2.3 (GND), IC3.3 (GND), J1.5, MCU.31 (VSS), MCU.45 (VSS), MCU.PAD (VSS), MCU.PAD@VIA01 (VSS), MCU.PAD@VIA02 (VSS), MCU.PAD@VIA03 (VSS), MCU.PAD@VIA04 (VSS), MCU.PAD@VIA05 (VSS), MCU.PAD@VIA06 (VSS), MCU.PAD@VIA07 (VSS), MCU.PAD@VIA08 (VSS), MCU.PAD@VIA09 (VSS), MCU.PAD@VIA10 (VSS), MCU.PAD@VIA11 (VSS), MCU.PAD@VIA12 (VSS), MCU.PAD@VIA13 (VSS), MCU.PAD@VIA14 (VSS), MCU.PAD@VIA15 (VSS), MCU.PAD@VIA16 (VSS), R2.2, R3.1, R5.1, R8.1, R11.1, Y3.2 (GND_1), Y3.4 (GND_2)
LEDA: LED1.1 (K), MCU.39 (P0.27)
MISO: ECG.18 (SDO), MCU.14 (P0.11)
MOSI: ECG.17 (SDI), MCU.12 (P0.10/NFC2)
unnamed: IC1.5 (PROG), R2.1
unnamed: IC1.1 (STAT), R13.1
unnamed: C13.1, MCU.1 (DEC1)
unnamed: LED1.2 (A), R7.1
unnamed: C11.1, MCU.46 (DEC4)
unnamed: C51.1, ECG.25 (VCM)
unnamed: C16.2, MCU.3 (P0.01/XL2), Y1.1
unnamed: C3.1, MCU.34 (XC1), Y3.1 (CRYSTAL_1)
unnamed: C4.1, L2.1, MCU.30 (ANT)
unnamed: E1.ANT (SIGNAL), L2.2
unnamed: C5.1, ECG.11 (CPLL)
unnamed: C48.1, ECG.10 (CAPN)
unnamed: C45.1, ECG.23 (VREF)
unnamed: C52.1, ECG.27 (VBG)
unnamed: C7.1, MCU.32 (DEC2)
unnamed: C48.2, ECG.9 (CAPP)
unnamed: C2.1, MCU.35 (XC2), Y3.3 (CRYSTAL_2)
unnamed: C8.1, MCU.33 (DEC3)
RESET: MCU.24 (P0.21/RESET), RESET.1
RXD: MCU.9 (P0.07), RXD.1
SCLK: ECG.16 (SCLK), MCU.11 (P0.09/NFC1)
SWCLK: MCU.25 (SWDCLK), SWCLK.1
SWDIO: MCU.26 (SWDIO), SWDIO.1
TXD: MCU.8 (P0.06), TXD.1
VBUS: C23.1, D2.A, IC1.4 (VDD), J1.1, Q3.1 (G), R3.2
VINBAT: C24.1, D2.C, IC2.2 (V_IN), IC3.2 (VIN), Q3.2 (S)
V_BATT: BATTERY.1, C19.1, IC1.3 (VBAT), Q3.3 (D), R6.2
XL1: C15.2, MCU.2 (P0.00/XL1), Y1.2

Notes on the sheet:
10K = 100mA
5.0K = 200mA
2.0K = 500mA
1.0K = 1000mA
Use USB Power if connected Gate = GND when no USB Gate = VBUS when USB (P CHANNEL MOSFET)
STAT Voltage = VDD-0.4 typ
@todo - Add a P MOSFET circuit to turn on and off the charger (to take voltage readings) - Work out R1 value - Design antenna for the transmitter (use ref design?)
POWER
BATT CHARGER
LDO 1.8V
ECG
MCU
LDO 3.3V
5mA I 3.3fV hence no resistor
Battery Level
LED0
SDWIO / JLINK

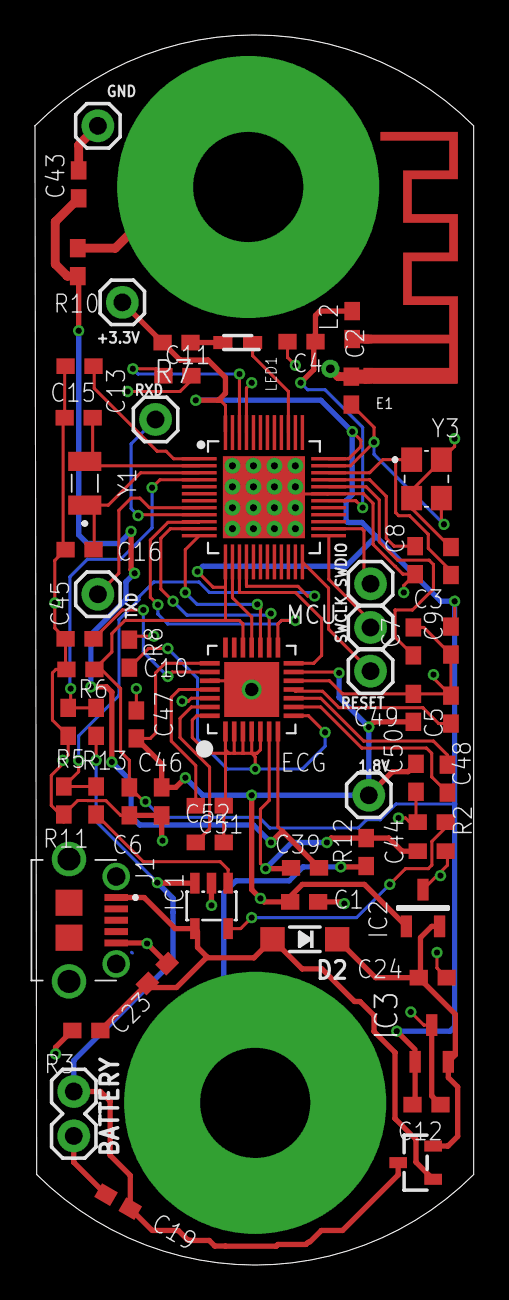
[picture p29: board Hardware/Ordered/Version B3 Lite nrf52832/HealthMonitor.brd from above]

Board: 2 copper layers, 25.1 x 70.4 mm, 61 parts (1 on the bottom side), 41 nets.

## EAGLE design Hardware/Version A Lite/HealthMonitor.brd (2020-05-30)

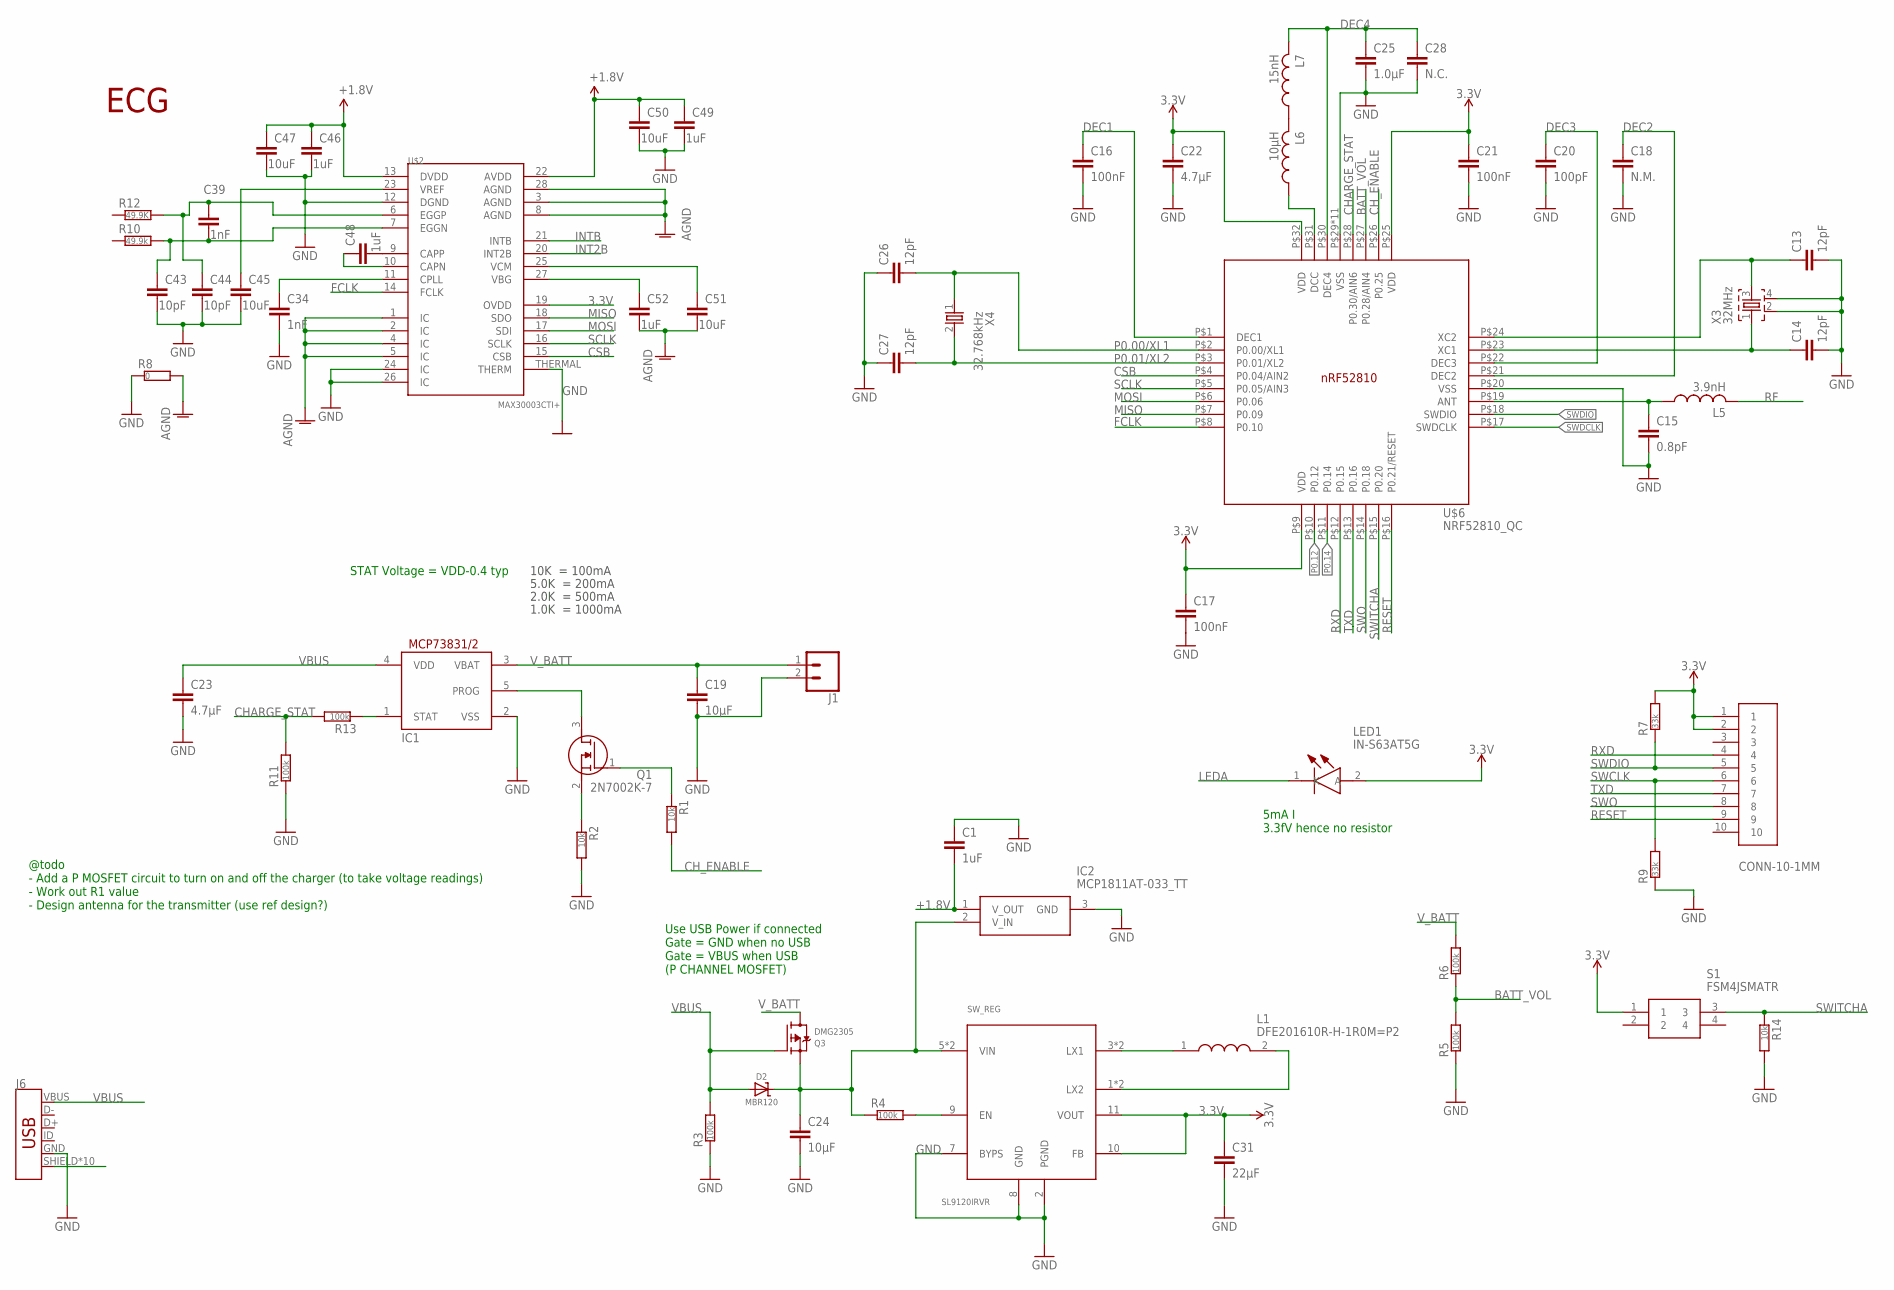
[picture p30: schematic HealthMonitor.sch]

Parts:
C1: 1uF; RESC0402_N
C13, C14, C26, C27: 12pF; RESC0402_N
C15: 0.8pF; RESC0402_N
C16, C17, C21: 100nF; RESC0402_N
C18: N.M.; RESC0402_N
C19, C24: 10µF; RESC0603_N
C20: 100pF; RESC0402_N
C22, C23: 4.7µF; RESC0603_N
C25: 1.0µF; RESC0603_N
C28: N.C.; RESC0402_N
C31: 22µF; RESC0603_N
C34: 1nF; C0805
C39: 1nF; RESC0603_N
C43, C44: 10pF; RESC0603_N
C45, C47, C50, C51: 10uF; RESC0603_N
C46, C48, C49, C52: 1uF; RESC0603_N
D2: MBR120; SOD-123
IC1: MCP73831/OT; SOT23-5L
IC2: MCP1811AT-033_TT; SOT95P237X112-3N
J1: CONN_02; 1X02
J6: USB_MICRO-B_HALF_PTH_MILL; USB-MICROB-PTH-MILL
L1: DFE201610R-H-1R0M=P2; INDC2016X100N
L5: 3.9nH; RESC0402_N
L6: 10µH; RESC0603_N
L7: 15nH; RESC0402_N
LED1: IN-S63AT5G; LEDM168X39N
Q1: 2N7002K-7; SOT96P240X100-3N
Q3: DMG2305; SOT23-R
R1, R2, R14: 10k; RESC0402_N
R3, R4, R5, R6, R11, R13: 100k; RESC0402_N
R7, R9: 33k; RESC0402_N
R8: 0; RESC0402_N
R10: 49.9k; RESC0402_N
R12: 49.9K; RESC0402_N
S1: FSM4JSMATR
SW_REG: SL9120IRVR; TQFN-12
U$1: CONN-10-1MM
U$2: MAX30003CTI+; QFN-28
U$6: NRF52810_QC; QFN50P500X500X90-32_N
X3: 32MHz; BT-XTAL_2016_N
X4: 32.768kHz; XTAL_3215_N

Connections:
3.3V: C17.1, C21.1, C22.1, C31.1, LED1.2 (A), R7.2, S1.1, SW_REG.10 (FB), SW_REG.11 (VOUT), U$1.1, U$1.2, U$2.19 (OVDD), U$6.P$9 (VDD), U$6.P$25 (VDD), U$6.P$32 (VDD)
+1.8V: C1.2, C46.1, C47.1, C49.1, C50.1, IC2.1 (V_OUT), U$2.13 (DVDD), U$2.22 (AVDD)
AGND: C51.2, C52.2, R8.2, U$2.1 (IC), U$2.2 (IC), U$2.3 (AGND), U$2.4 (IC), U$2.5 (IC), U$2.8 (AGND), U$2.28 (AGND)
ANT1: C15.1, L5.1, U$6.P$19 (ANT)
BATT_VOL: R5.2, R6.1, U$6.P$27 (P0.28/AIN4)
CHARGE_STAT: R11.2, R13.2, U$6.P$28 (P0.30/AIN6)
CH_ENABLE: R1.2, U$6.P$26 (P0.25)
CSB: U$2.15 (CSB), U$6.P$4 (P0.04/AIN2)
DEC1: C16.1, U$6.P$1 (DEC1)
DEC2: C18.1, U$6.P$21 (DEC2)
DEC3: C20.1, U$6.P$22 (DEC3)
DEC4: C25.1, C28.1, L7.2, U$6.P$30 (DEC4)
ECGN1: C39.2, C43.1, R10.2, U$2.7 (EGGN)
ECGP1: C39.1, C44.1, R12.2, U$2.6 (EGGP)
FCLK: U$2.14 (FCLK), U$6.P$8 (P0.10)
GND: C1.1, C13.2, C14.2, C15.2, C16.2, C17.2, C18.2, C19.2, C20.2, C21.2, C22.2, C23.2, C24.2, C25.2, C26.1, C27.1, C28.2, C31.2, C34.2, C43.2, C44.2, C45.2, C46.2, C47.2, C49.2, C50.2, IC1.2 (VSS), IC2.3 (GND), J1.2, J6.GND, R2.2, R3.1, R5.1, R8.1, R9.1, R11.1, R14.2, SW_REG.2 (PGND), SW_REG.7 (BYPS), SW_REG.8 (GND), U$2.12 (DGND), U$2.24 (IC), U$2.26 (IC), U$2.THERMAL (THERM), U$6.P$20 (VSS), U$6.P$29 (VSS), U$6.P$33 (VSS), U$6.P$34 (VSS), U$6.P$35 (VSS), U$6.P$36 (VSS), U$6.P$37 (VSS), U$6.P$38 (VSS), U$6.P$39 (VSS), U$6.P$40 (VSS), U$6.P$41 (VSS), U$6.P$42 (VSS), X3.2, X3.4
INT2B: U$2.20 (INT2B)
INTB: U$2.21 (INTB)
LEDA: LED1.1 (K)
MISO: U$2.18 (SDO), U$6.P$7 (P0.09)
MOSI: U$2.17 (SDI), U$6.P$6 (P0.06)
unnamed: R4.2, SW_REG.9 (EN)
unnamed: IC1.1 (STAT), R13.1
unnamed: Q1.2 (S), R2.1
unnamed: Q1.1 (G), R1.1
unnamed: L1.1, SW_REG.3 (LX1), SW_REG.4 (LX1)
unnamed: C24.1, D2.C, IC2.2 (V_IN), Q3.2 (S), R4.1, SW_REG.5 (VIN), SW_REG.6 (VIN)
unnamed: IC1.5 (PROG), Q1.3 (D)
unnamed: L1.2, SW_REG.1 (LX2), SW_REG.12 (LX2)
unnamed: C51.1, U$2.25 (VCM)
unnamed: C13.1, U$6.P$24 (XC2), X3.3
unnamed: L6.2, L7.1
unnamed: L6.1, U$6.P$31 (DCC)
unnamed: C34.1, U$2.11 (CPLL)
unnamed: C48.1, U$2.10 (CAPN)
unnamed: C45.1, U$2.23 (VREF)
unnamed: C52.1, U$2.27 (VBG)
unnamed: C48.2, U$2.9 (CAPP)
P0.00/XL1: C26.2, U$6.P$2 (P0.00/XL1), X4.1
P0.01/XL2: C27.2, U$6.P$3 (P0.01/XL2), X4.2
P0.12: U$6.P$10 (P0.12)
P0.14: U$6.P$11 (P0.14)
RESET: U$1.9, U$6.P$16 (P0.21/RESET)
RF: L5.2
RXD: U$1.4, U$6.P$12 (P0.15)
SCLK: U$2.16 (SCLK), U$6.P$5 (P0.05/AIN3)
SHIELD: J6.SHIELD, J6.SHIELD2 (SHIELD), J6.SHIELD3 (SHIELD), J6.SHIELD4 (SHIELD), J6.SHIELD5 (SHIELD), J6.SHIELD6 (SHIELD), J6.SHIELD7 (SHIELD), J6.SHIELD8 (SHIELD), J6.SHIELD9 (SHIELD), J6.SHIELD10 (SHIELD)
SWCLK: R9.2, U$1.6
SWDCLK: U$6.P$17 (SWDCLK)
SWDIO: R7.1, U$1.5, U$6.P$18 (SWDIO)
SWITCHA: R14.1, S1.3, U$6.P$15 (P0.20)
SWO: U$1.8, U$6.P$14 (P0.18)
TXD: U$1.7, U$6.P$13 (P0.16)
VBUS: C23.1, D2.A, IC1.4 (VDD), J6.VBUS, Q3.1 (G), R3.2
V_BATT: C19.1, IC1.3 (VBAT), J1.1, Q3.3 (D), R6.2
X2: C14.1, U$6.P$23 (XC1), X3.1

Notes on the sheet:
10K = 100mA
5.0K = 200mA
2.0K = 500mA
1.0K = 1000mA
Use USB Power if connected Gate = GND when no USB Gate = VBUS when USB (P CHANNEL MOSFET)
ECG
STAT Voltage = VDD-0.4 typ
@todo - Add a P MOSFET circuit to turn on and off the charger (to take voltage readings) - Work out R1 value - Design antenna for the transmitter (use ref design?)
5mA I 3.3fV hence no resistor

Board: 2 copper layers, 63 parts (0 on the bottom side), 49 nets, no tracks yet.

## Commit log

2020-03-11 ECG Data reading + UART working on custom board but not BLE, BLE + SPI Read causes a crash am not sure why.
2020-03-12 timer 3 interrupt test with led working
2020-03-12 BLE working moved to a seperate file Fix battery measurement adc issue removed unused files
2020-03-12 adc pin changes sdk config to increase resolution
2020-05-30 Restructure, Hardware files, Documents
    Added: hardware files (all of the versions)
    Specification, Poster, and final report a
    [BOM B1 Advanced 31 01 2020 v2.xlsx, BOM B1 Advanced 31 01 2020.XLSX, BOM VB1.xlsx, HealthMonitor.brd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]

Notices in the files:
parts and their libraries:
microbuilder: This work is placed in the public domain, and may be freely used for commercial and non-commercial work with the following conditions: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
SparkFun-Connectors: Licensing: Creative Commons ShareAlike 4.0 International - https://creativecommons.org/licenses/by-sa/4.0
